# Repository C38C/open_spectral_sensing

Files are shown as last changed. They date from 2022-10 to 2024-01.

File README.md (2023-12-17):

# Open Spectral Sensing

## Table of Contents
1. [About the Project](#about-the-project)
1. [Overview](#overview)
1. [Getting Started](#getting-started)
1. [Capturing Data](#capturing-data)
1. [Build Guide](#build-guide)
1. [Calibration](#calibration)
1. [Troubleshooting](#troubleshooting)
1. [Credits](#credits)

<h2 id="about-the-project">About the Project</h2>
Visible light is made up of several individual wavelengths, each with their own power level. By measuring the power distribution of light throughout the spectrum, we can begin to identify light and quantify its qualities. A spectral sensor measures the power levels at each wavelength. This data can be used for various use-cases such as in colour calibration, agriculture, health, and more. 

<h2 id="overview">Overview</h2>
The sensor is programmed using Arduino (C++) and communicates via a Python program. The sensor consists of off-the-shelf components from SparkFun, and a spectral sensor from nanoLambda - producing an easy-to-assemble spectral sensing device. The goal of this project is to create an open-source and affordable spectral sensing device in order to make light research more accessible.

<h2 id="getting-started">Getting Started</h2>

For wiring, and assembly instructions, see the [Build Guide](#build-guide).

<h3>Installation</h3>

- You must first install the firmware onto the device using provided [compiled binaries](https://github.com/C38C/open_spectral_sensing/releases) by following the instructions below:
    
    - Connect the sensor to a computer via USB
    - With the sensor powered on, double tap the RESET button on the side. (If the sensor is enclosed in the case, you can use an M2 allen-key through the provided hole on the side of the case). This will bring up the "NRF52BOOT" sensor folder.
    - Drag and drop the compiled binary (.uf2) file into this new folder. The sensor will automatically disconnect and update the firmware.
    - Disconnect and reconnect the sensor.

- To connect to the sensor using ```dock.py```, first install matplotlib and pySerial.
```
$ pip install matplotlib
$ pip install pyserial
```

- (Optional) To build your own firmware using the provided source, you must install Arduino IDE and the following libraries:

    - Install Arduino IDE: https://www.arduino.cc/en/software
    - NSP32-Library: https://github.com/arsalan1322/NSP32-Library
    - Installing the Arduino Core for nRF52 Boards: https://learn.sparkfun.com/tutorials/nrf52840-development-with-arduino-and-circuitpython
    - Time library: https://github.com/PaulStoffregen/Time

<h3>Usage</h3>

Once you have assembled the sensor, and flashed the firmware, and installed the required Python packages, you can connect to it using the ```dock.py``` program.
```
$ python dock.py
```
The program will begin looking for a connected spectral sensor, connect to it, then display the menu below. From this menu, you can see the sensor name, sensor port, the current status of the sensor, as well as the current recording interval in ms. You can also start a manual recording, or change other sensor settings. 

```
Refreshed.
---
Selected device: NSP_A on port: COM20.
Currently PAUSED. Recording interval is set to 60000
---
[1] START_RECORDING
[2] MANUAL_CAPTURE
[3] EXPORT_ALL (0 entries)
[4] ERASE_STORAGE
[5] SET_COLLECTION_INTERVAL
[6] SET_DEVICE_NAME
[7] SET_CALIBRATION_FACTOR
[8] RESET_DEVICE
[9] DISCONNECT
[10] CONFIGURE_NSP
[11] REFRESH
Choose a command by entering the number in front
>
```
From here, you can enter ```10``` to enter ```CONFIGURE_NSP``` which will guide you through setting up the sensor for quickly capturing data. 

Alternatively, you can set the recording interval by entering ```5```, then start the recording by entering ```1```. Then, you can disconnect the device by entering ```9```. This step does not set the device name, and uses default capture settings.

At this point, you can disconnect the USB cable if the device is already connected to the battery. The device will continue to collect data according to the interval you set. 

<i>Note that if the device powers off somehow due to a disconnected battery or lack of charge, it will stop recording until started again through</i> ```dock.py```.

<h4>Reading Data </h4>

Enter ```3``` to export all data stored on the device onto the connected computer. Look for a "data" folder in the same directory as ```dock.py```. 

For large files that contain over 500 data points, it is recommended to read data directly off the microSD by ejecting it from the sensor. The microSD can be accessed by removing the cap only.

<h4>Data Structure</h4>

Data is stored on the sensor in a CSV format. There are 146 columns. Columns 1 - 11 hold information about the spectral measurement, and columns 12 - 146 hold the spectral power distribution at 5 nm intervals from 340 nm to 1010 nm. Each row is a unique captured data point.

| Column # | Column title | Example data | Range    | Description                                                                                                       |
|----------|--------------|--------------|----------|-------------------------------------------------------------------------------------------------------------------|
| 1        | DATE         | 05/10/2022   | -        | The date on which this data point was captured. |
| 2        | TIME         | 12:30:37     | -        | The time on which this data point was captured. |
| 3        | MANUAL       | 1            | 0 or 1   | Was this data point captured manually? 1 if yes, 0 if no. |
| 4        | INT_TIME     | 448          | 1 - 1000 | The integration time used for this data point. Exposure time (ms) = (896*[IntegrationTime] + 160) / 500 |
| 5        | FRAME_AVG    | 3            | 1 - 10   | How many frames where averaged for this data point. |
| 6        | AE           | 1            | 0 or 1   | Was auto-exposure enabled? 1 fi yes, 0 if no. |
| 7        | QUALITY      | 0            | -1 to 1   | Indicates whether data point was captured under poor lighting conditions. -1 means too dark, 0 is normal, 1 is too bright. Data points that are not 0 should be discarded. |
| 8        | X            | 38.61        | -        | CIE1931 X value. |
| 9       | Y            | 37.52        | -        | CIE1931 Y value. |
| 10       | Z            | 21.73        | -        | CIE1931 Z value. |
| 11 - 145       | 340 - 1010            |  -       | -        | spectral power in W/m<sup>2</sup>. |

<h4>Charging</h4>

The device will automatically turn off when the battery voltage is too low. Simply plug the sensor into a computer via USB to begin charging. See [LEDs](#leds) for charging indicator.

<h4 id="leds">LEDs</h4>

The sensor has three on-board LEDs: red, blue, and orange. The red LED is always on when the sensor is powered on. The orange LED is only on when the battery is charging, off when charge complete or battery is not connected. 

The blue LED behaviour can be classified using the following list:

- Solid on when sensor has not been setup and it is not recording.
- On for a brief moment while sensor is collecting data, off otherwise.
- Flashes to indicate a problem. See [Troubleshooting](#troubleshooting).

<h2 id="capturing-data">Capturing Data</h2>

There are two ways to capture data using the sensor.

<h3>Automatic and Manual Capture</h3>

<h4>Automatic</h4>

Automatic capture is when you plug in the device, and start recording via the ```START_RECORDING``` menu option in ```dock.py```. The recording interval must be set. Recording will last until stopped via the dock program, or if power is lost.

<h4>Manual Capture</h4>

With the device plugged in and connected to the dock program, you can initiate a data point capture by selecting ```[2] MANUAL_CAPTURE```. A recording interval does not need to be set for this mode. The device will capture one measurement and save it to device memory.

With this feature, you can also preview a graph of the data point once captured. 

<h3>Reading Data</h3>

Data is stored in a CSV file on the microSD card. Data can be read directly from the microSD card, or through the ```EXPORT_ALL``` option via the dock program.

<h2 id="build-guide">Build Guide</h2>

<h3>Parts List</h3>

Electronics

1. [nanoLambda NSP32m W1](https://nanolambda.myshopify.com/products/nsp32m_w1_temp)
2. [SparkFun Pro nRF52840 Mini](https://www.sparkfun.com/products/15025)
3. [SparkFun microSD Transflash Breakout](https://www.sparkfun.com/products/544)
4. 2GB+ microSD card
5. [800mAh Li-Po battery with 2mm JST connector](https://www.solarbotics.com/product/17804)
6. [30 AWG Silicone Wire](https://www.amazon.ca/gp/product/B01M70EDCW/ref=ppx_yo_dt_b_asin_title_o04_s00?ie=UTF8&psc=1)

Hardware (optional)

6. [3D printed case ]() (Found in ```3D Models\Case```)
7. [2x] M2 bolts and [2x] nuts (for cap)
8. [4x] 4x1.7mm cylindrical magnets

<h3 id="wiring-diagram">Wiring Diagram</h3>

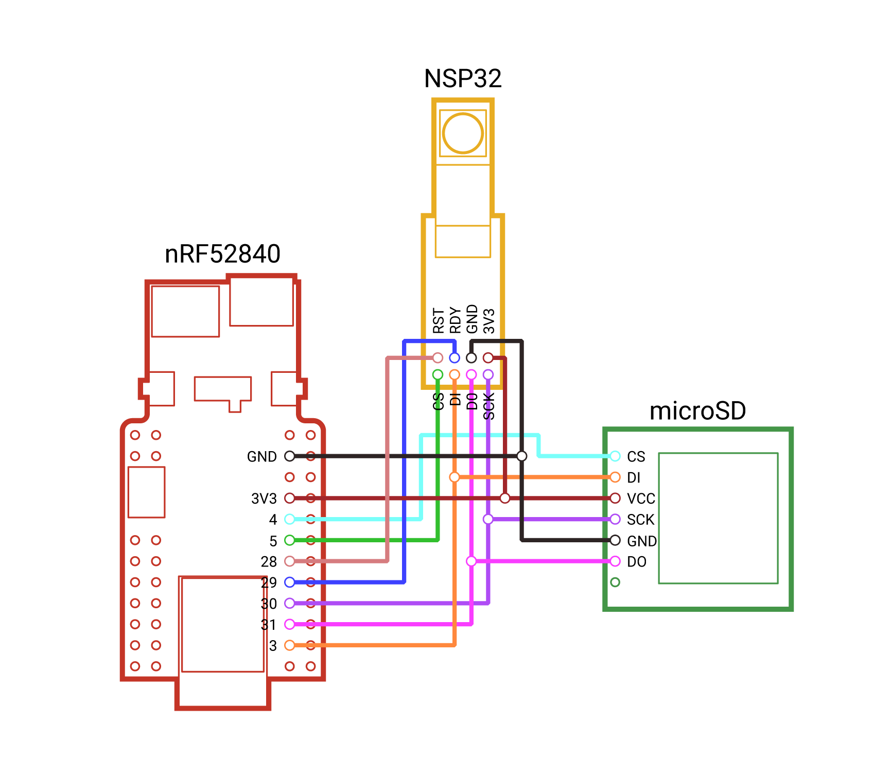
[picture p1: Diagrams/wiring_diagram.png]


<h3 id="layout">Layout</h3>

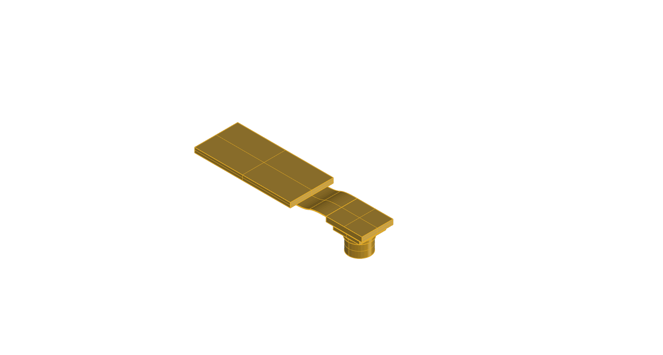
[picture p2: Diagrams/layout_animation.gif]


<h3>Soldering</h3>

To allow for a small device footprint, flexible 30 AWG silicone wire is used. Approximately 60 cm of wire is used for the configuration outlined in [Layout](#layout)

Soldering happens from both the top and bottom of the nRF52840. "Helping hands" are highly recommended, as well as a fine-tip soldering iron.

Use the following table to help cut, match, and solder wires:

| Wire  # | Length for SD (mm) | Length for NSP (mm) | Pin on nRF52840 | Pin on microSD card reader | Pin on nanoLambda NSP32m |
|---------|--------------------|---------------------|-----------------|----------------------------|--------------------------|
| 1       | 20                 | 55                  | GND             | GND                        | GND                      |
| 2       | 25                 | 50                  | 3V3             | VCC                        | 3V3                      |
| 3       | 20                 | -                   | 4               | CS                         | -                        |
| 4       | -                  | 45                  | 5               | -                          | CS                       |
| 5       | -                  | 45                  | 28              | -                          | RST                      |
| 6       | -                  | 40                  | 29              | -                          | RDY                      |
| 7       | 40                 | 45                  | 30              | SCK                        | SCK                      |
| 8       | 50                 | 35                  | 31              | DO/MISO                    | DO/MISO                  |
| 9       | 40                 | 45                  | 3               | DI/MOSI                    | DI/MOSI                  |

Wires for the microSD card reader are soldered from the bottom, wires for the NSP32m are soldered from the top.
Two wires connect to single common pins on the nRF52840 for GND, 3V3, SCK, DO, and DI.

<h3>3D Printing</h3>

The case consists of three separate parts that come together to enclose the sensor. They are located in the ```3D Models\Case``` directory.

<h4>Material</h4>
PETG (recommended), PLA, ABS, etc. Recommended material is PETG due to its flexibility. PLA and ABS can be used, but repeated strain may cause parts to snap.

<h4>Layer height</h4>
0.12 mm or finer.

<h4>Supports</h4>
Yes, as shown in orange.

<h4>Part orientation</h4>

**If using FDM printer, the part orientation is important for maximum strength.**

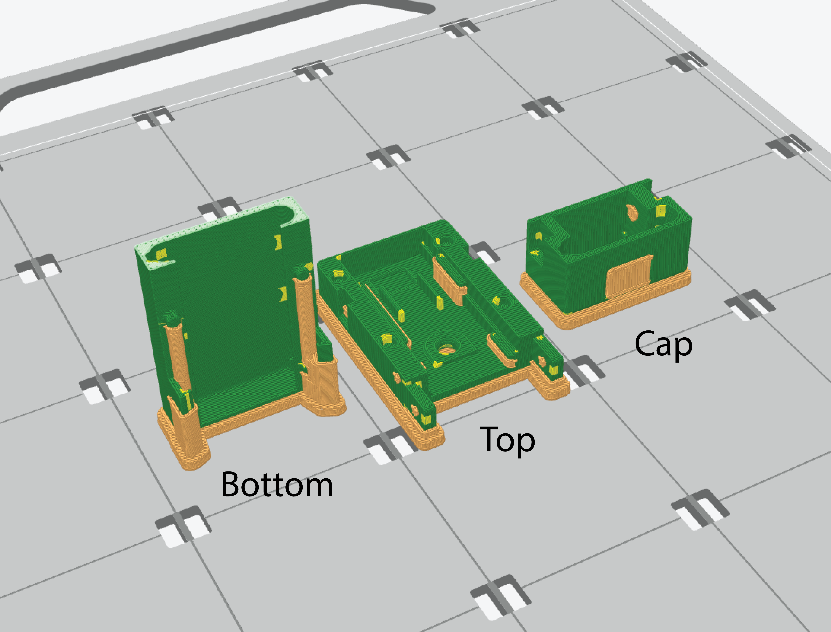
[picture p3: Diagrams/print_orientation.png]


<h3>Assembly</h3>

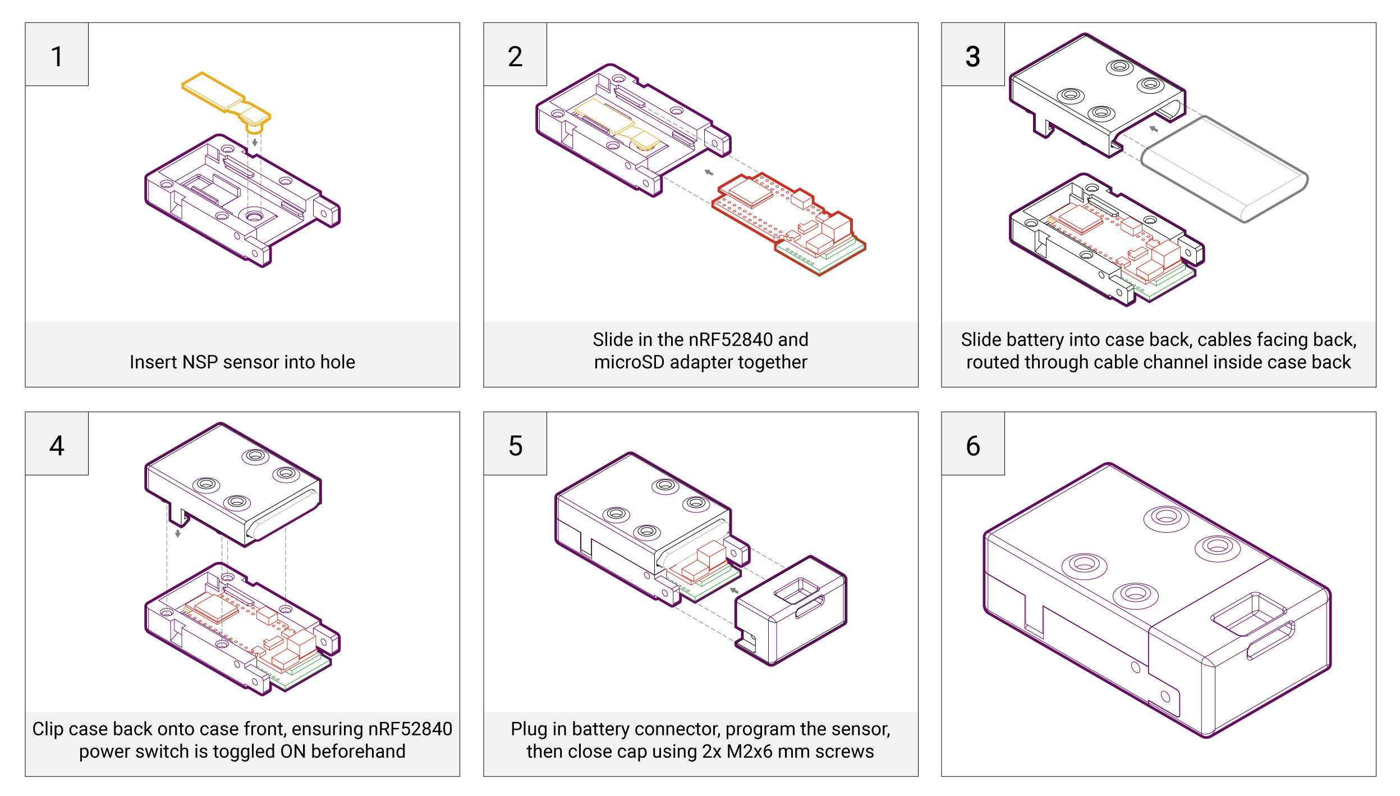
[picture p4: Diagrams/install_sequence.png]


&nbsp;

1. Insert the NSP32m sensor through the hole in the ```top``` part of the case
2. Slide in the nRF52840 while gently pushing down the NSP32m, ensuring the microSD reader slides in to its slot when the nRF52840 is half-way inserted.
3. Slide the battery into the ```bottom``` part of the case as shown. The cable will come around to the front through the channel on the side.
4. Snap together both the ```bottom``` and ```top``` parts of the case, making sure the silicone wires are out of the way.
5. Fit two M2 hex bolts into the ```cap```. They are compression fit.
6. **Before installing the ```cap```, make sure to program the sensor, as the USB port is inaccessible with the ```cap``` on.**
6. *Once the sensor has been programmed*, slide the ```cap``` onto the case, lining up the forks on the sides.
7. Screw in two M2x8mm bolts through the forks. 
8. (optional) Insert lanyard loop.

*The sensor is not waterproof, please keep it dry.*

<h2 id="calibration">Calibration</h2>

If you are using a non power-calibrated (NPC) sensor from nanoLambda, you must calibrate it against another calibrated sensor and update the calibration factor within your NPC sensor. Use the ```SET_CALIBRATION_FACTOR``` option inside the dock program.

<h2 id="troubleshooting">Troubleshooting</h2>

<h3>Blue LED flashes once: Problem with SD card.</h3>

1. Check if SD card is inserted
2. Plug in SD card to computer and delete all files stored on it

<h3>Blue LED flashes twice: Problem with internal memory</h3>

1. Connect the sensor to ```dock.py```
2. Select ```RESET_DEVICE``` by entering ```4```

<h2 id="resources">Resources</h2>
<ul>
<li>Microsoft UF2: <a href="https://github.com/microsoft/uf2">https://github.com/microsoft/uf2</a></li>
</ul>

<h2 id="credits">Credits</h2>

- J. Alstan Jakubiec
Assistant Professor, Daniels Faculty of Architecture + School of the Environment
alstan.jakubiec@daniels.utoronto.ca
- Sadi Wali
Research Assistant, B.A.Arch
- Arsalan Khan
B.A.Sc. Physics and Computer Science Student

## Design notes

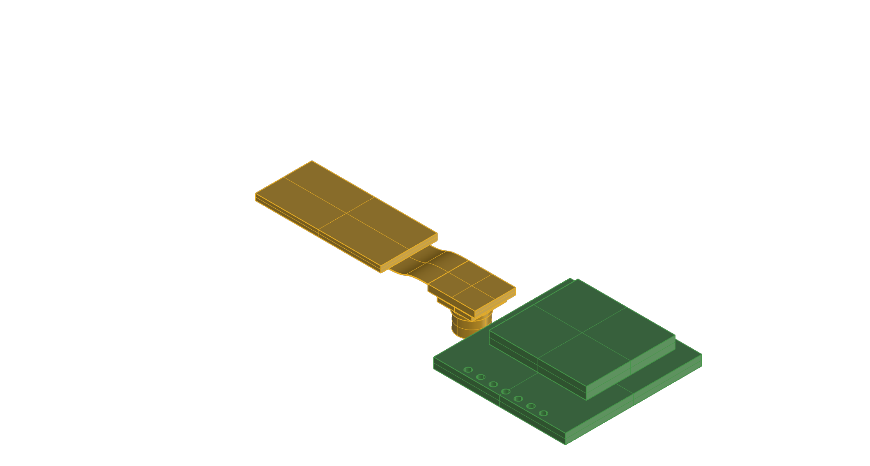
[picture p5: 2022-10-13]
Diagrams/layout_2.png

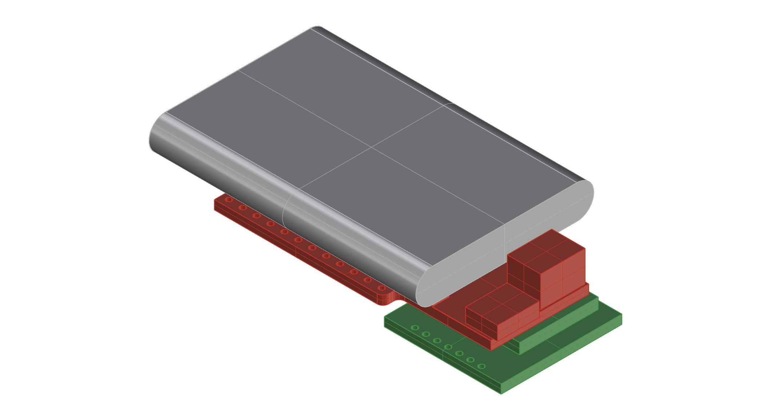
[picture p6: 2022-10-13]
Diagrams/layout_4.png

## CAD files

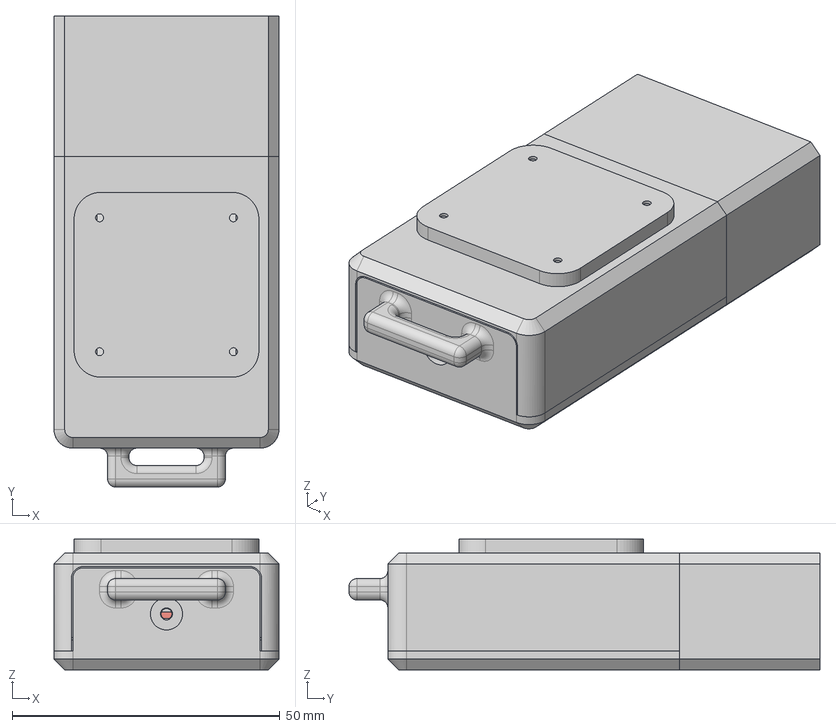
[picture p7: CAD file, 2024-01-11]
3D Models/Case V2/OOSI_CASE_V2.step
42.0 x 87.9 x 24.4 mm
Battery
SD
NL
nrf52
CASE_A
CASE_B
backplate
cover
SD_CARD_PROTECTOR

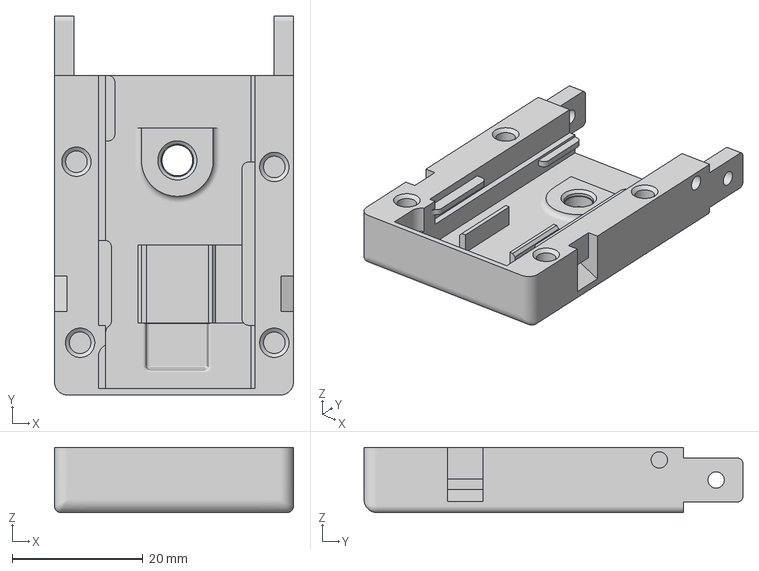
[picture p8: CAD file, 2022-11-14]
3D Models/Case/case_front.3mf
36.6 x 58.0 x 10.0 mm

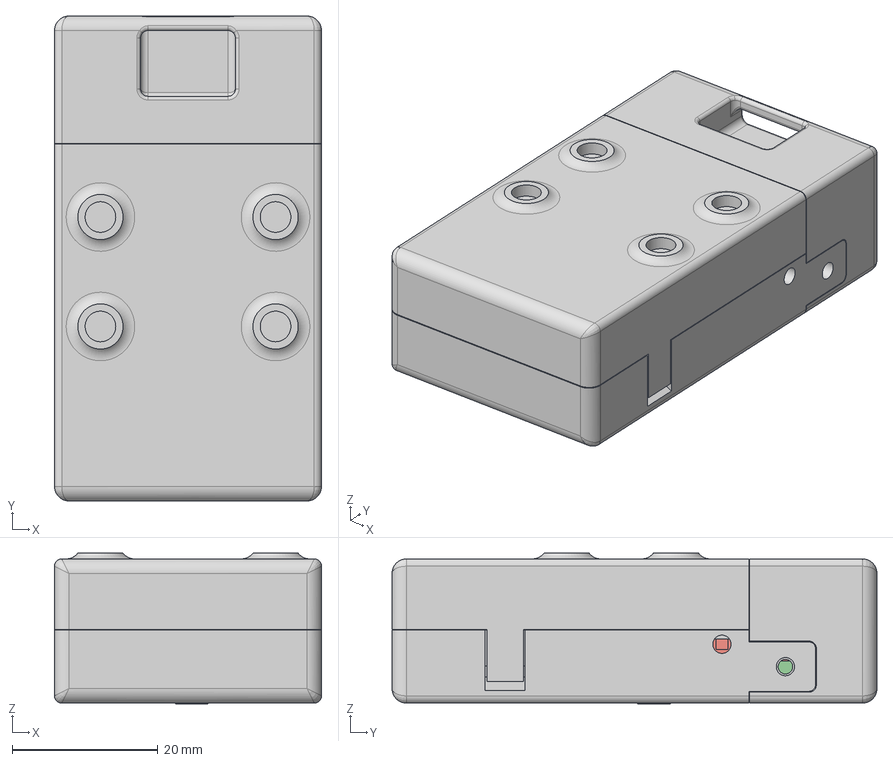
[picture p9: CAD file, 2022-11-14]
3D Models/Case/open_spectral_sensor_case_v1.step
36.6 x 66.5 x 20.7 mm
Battery
SD
NL_1
nrf52
Case Back
Case Cap
Case Front

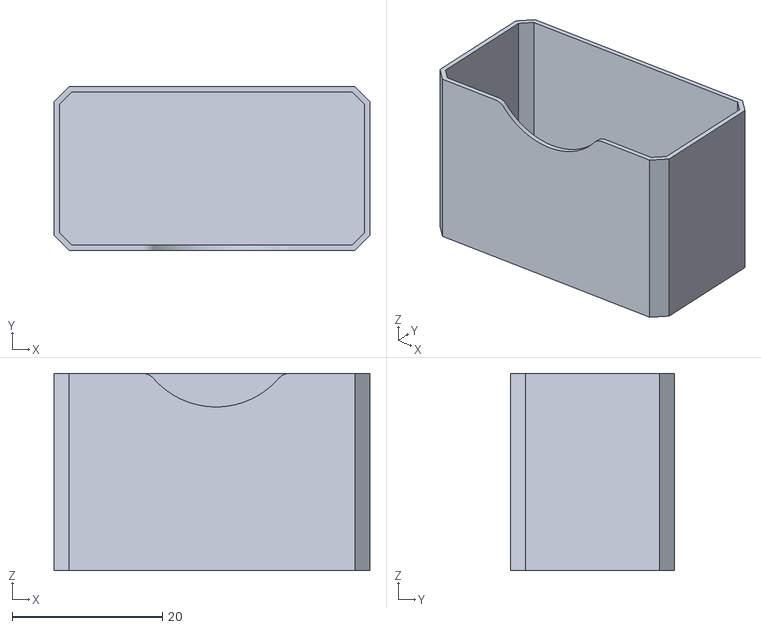
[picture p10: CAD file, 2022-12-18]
3D Models/Case V2/CASE_CAP.stl
42.0 x 21.8 x 26.2

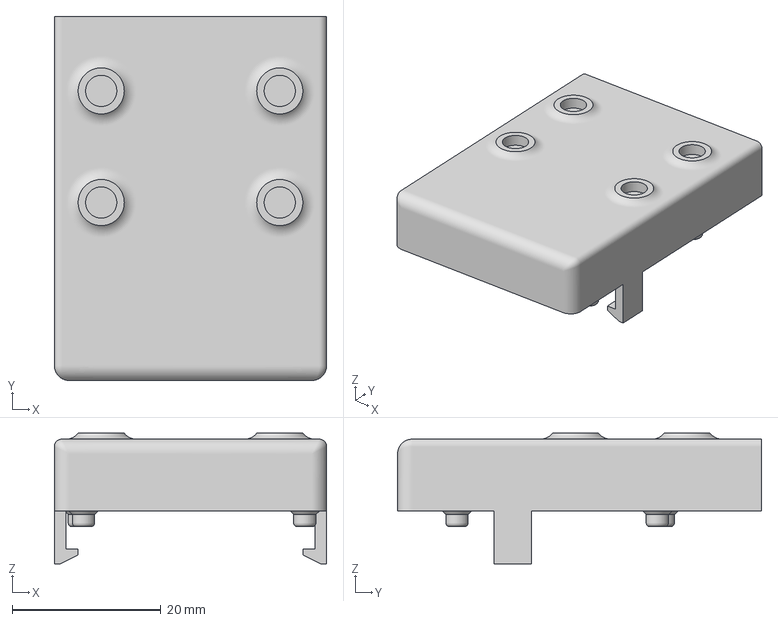
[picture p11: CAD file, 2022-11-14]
3D Models/Case/case_back.3mf
36.6 x 48.9 x 17.6 mm

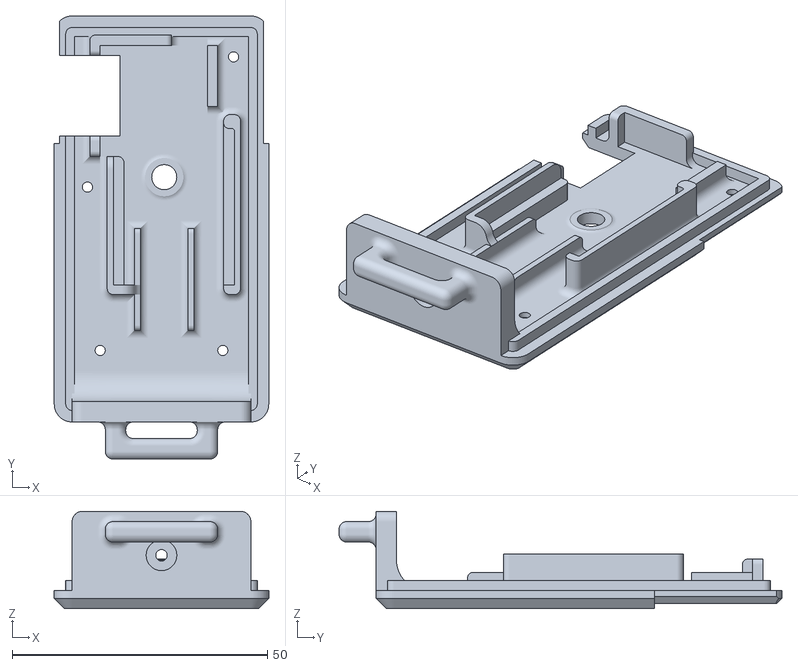
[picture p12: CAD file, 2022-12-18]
3D Models/Case V2/CASE_FRONT.stl
42.0 x 86.7 x 19.0

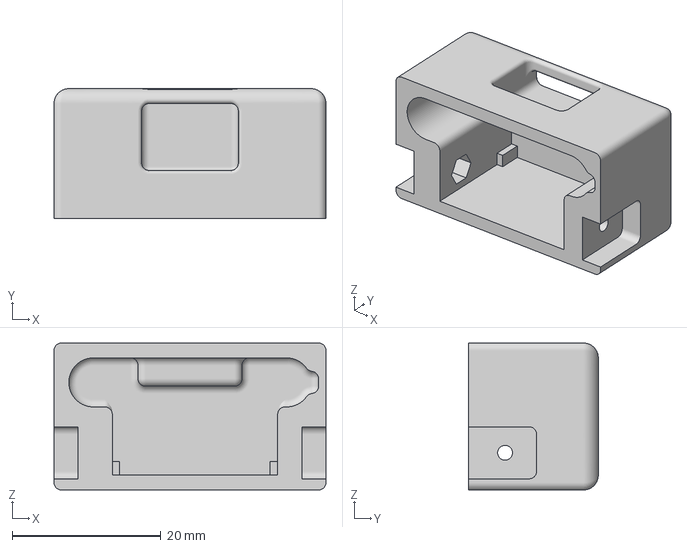
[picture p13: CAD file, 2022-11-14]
3D Models/Case/case_cap.3mf
36.6 x 17.4 x 19.8 mm

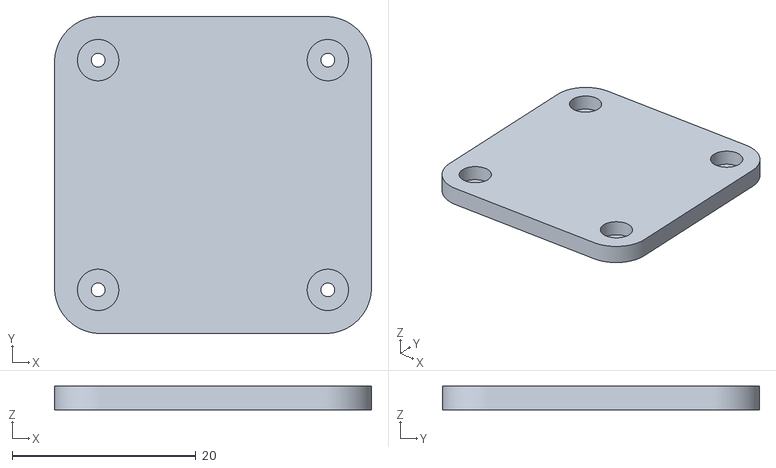
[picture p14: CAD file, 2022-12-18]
3D Models/Case V2/CASE_MAGNETIC_BACKPLATE.stl
34.5 x 34.5 x 2.60

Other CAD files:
3D Models/Case V2/CASE_SDCARD_HOLDER.stl
3D Models/Case V2/OOSI_CASE_V2.f3d
3D Models/Case/open_spectral_sensor_case_v1.f3d

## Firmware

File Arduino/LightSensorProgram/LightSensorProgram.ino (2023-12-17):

/**
 * Sadi Wali August 2022
 * Last modified: December 16 2023
 * 
 * This open-source program is written for the Nordic nRF52840, and the NanoLambda NSP32m W1
 * to create a lightweight wearable spectral sensor that record data at a set interval on battery.
 * 
 * Pin layout used:
 * ------------------------------------
 *               NSP32      Sparkfun       
 * SPI                      nRF52840     
 * Signal        Pin          Pin        
 * ------------------------------------
 * Wakeup/Reset  RST          28    
 * SPI SSEL      SS           5    
 * SPI MOSI      MOSI         3    
 * SPI MISO      MISO         31  
 * SPI SCK       SCK          30   
 * Ready         Ready        29
 * ------------------------------------
 *               SD Card
 *               Pin
 * ------------------------------------
 * SPI SSEL      CS           4
 * SPI MOSI      DI           3
 * SPI MISO      DO           31
 * SPI SCK       SCK          30
 * 
 * 
 * 
 * Error codes:
 * ------------------------------------
 * 
 * Error         Number of
 *               flashes
 * ------------------------------------
 * SD card       1
 * Internal FS   2
 * 
 * 
 **/

#include "Adafruit_TinyUSB.h"                       // for serial communication on nrf52840

#include <SPI.h>                                    // Arduino SPI

#include <TimeLib.h>                                // Date and time

#include <ArduinoAdaptor.h>                         // for low-level interfacing with the NSP via Arduino

#include <NSP32.h>                                  // for high-level interfacing with the NSP module

#include "DataStorage.h"                            // SD Data storage module

#include "Constants.h"                              // constants

#include <Adafruit_LittleFS.h>                      // persistent data storage

#include <InternalFileSystem.h>                     // persistent data storage

using namespace NanoLambdaNSP32;
using namespace Adafruit_LittleFS_Namespace;

const unsigned int PinRst = NSP_RESET;              // pin Reset
const unsigned int PinSS = NSP_CS_PIN;              // NSP chip select pin
const unsigned int PinReady = NSP_READY;            // pin Ready

// VARIABLES
int logging_interval = DEF_CAPTURE_INTERVAL;        // the data logging interval
unsigned long last_collection_time = 0;             // remember the last collection interval
unsigned long time_offset = 0;                      // how much time to offset by if device hung for long operations
bool recording = false;                             // is data capture recording?
String device_name = DEV_NAME_PREFIX;               // the device name for easier identification
double calibration_factor = DEF_CALIBRATION_FACTOR; // the calibration factor
int int_time = 500;                                 // default integration time for sensor           
int frame_avg = DEF_FRAME_AVG;                      // how many frames to average
bool ae = true;                                     // use autoexposure?
unsigned int data_counter = 0;                      // how many data points collected and stored
int s_dark_readings = 0;                            // how many sequential dark readings?
unsigned long paused_time = 0;                      // when was the sensor paused
unsigned long pause_duration = 0;                   // how long was the sensor paused for?

char ser_buffer[32];                                // the serial buffer
int read_index = 0;                                 // the serial buffer read index

// OBJECTS
ArduinoAdaptor adaptor(PinRst, PinSS);              // master MCU adaptor
NSP32 nsp32( & adaptor, NSP32::ChannelSpi);         // NSP32 (using SPI channel)
Storage st(SD_CS_PIN, LOG_FILENAME);                // the data storage object
Adafruit_LittleFS_Namespace::File file(InternalFS); // the metadata file stored in persistent flash


/* Arduino setup function. */
void setup() {
  pinMode(PinReady, INPUT_PULLUP); // use pull-up for ready pin
  pinMode(7, OUTPUT); // onboard LED output
  digitalWrite(7, HIGH); // turn LED ON
  attachInterrupt(digitalPinToInterrupt(PinReady),
    PinReadyTriggerISR, FALLING); // enable interrupt for NSP READY
  // initialize serial port
  Serial.begin(BAUDRATE);

  // initialize the persistent storage
  InternalFS.begin();

  // read persistent flash storage into memory
  read_memory();

  // if the SD storage object is errored, go into error state
  if (!st.init()) error_state(1);

  // initialize NSP32
  nsp32.Init();
  nsp32.Standby(0);

  // if device is already recording on startup, that means power was lost
  if (recording) {
    String error_line = "POWER LOSS DETECTED";
    st.write_line(& error_line);
  }
  
}

/* Get a reading from the NSP32 sensor */
void read_sensor(SpectrumInfo * info, int use_int_time = 0, int use_frame_avg = 3, bool use_ae = true) {
  // wakeup the sensor if sleeping
  nsp32.Wakeup();
  // get the spectrum data. Note that if ae is true, int_time is ignored
  nsp32.AcqSpectrum(0, use_int_time, use_frame_avg, use_ae);
  // wait until spectrum data completely collected
  while (nsp32.GetReturnPacketSize() <= 0) nsp32.UpdateStatus();
  // data has been collected, extract into info
  nsp32.ExtractSpectrumInfo(info);
}

/* Check if datapoint is too dark, okay, or too bright indicated by -1, 0, 1 respectively */
int validate_reading(SpectrumInfo infoS) {

  // count the number of dips to zero. A dark reading will have multiple dips
  int dip_count = 0;
  bool is_zero = false;
  
  // go through 400 - 700 nm, and count how many times the graph dips to 0
  for (int i = (400 - MIN_WAVELENGTH) / 5; i < (700 - MIN_WAVELENGTH) / 5; i++) {
     if (infoS.Spectrum[i] == 0) {
      if (!is_zero) {
        dip_count++;
        is_zero = true;
      }
     } else {
      is_zero = false;
     }
  }

  // combine the dip count with autoexposure malfunction with low CIE1931 Y value 
  if (infoS.IntegrationTime == 1 || infoS.Y <= MIN_ACCEPTABLE_Y || dip_count >= 2) {
    // too dark
    return -1;
  } else if (infoS.IsSaturated == 1) {
    // too bright
    return 1;
  } else {
    // just right
    return 0;
  }
}

/* Take a manual or automatic measurement, and return the formatted datapoint line */
String take_measurement(bool manual_measurement = false) {
  SpectrumInfo infoS; // variable for storing the spectrum data

  bool dark_flag = true;
  bool too_dark = false;
  bool second_attempt = false;

  // modified settings to use in this session
  int mod_int_time = int_time;
  int mod_frame_avg = frame_avg;
  bool mod_ae = ae;

  while (true) {

    read_sensor( & infoS, mod_int_time, mod_frame_avg, mod_ae);
    
    // validate the datapoint
    int validation_res = validate_reading(infoS);

    if (validation_res == 1) {
      // too bright, nothing to do
      s_dark_readings = 0;
      break;

    } else if (validation_res == -1) {
      // too dark
      
      if (ENABLE_NIGHTMODE && s_dark_readings >= MAX_DARK_READINGS) {
        // too many dark readings in a series
        
        if (!second_attempt) {
          // this was the first attempt, set int_time to 500, and try again
          mod_ae = false;
          second_attempt = true;
          mod_int_time = STARTING_DARK_INT_TIME;
          continue;
          
        } else {
          // this was the second attempt, environment still too dark so don't continue
          too_dark = true;
          break;
          
        }
      }

      // too dark even with int_time maxed
      if (mod_int_time >= MAX_INT_TIME) {
        too_dark = true;
        s_dark_readings++;
        break;
      }

      // find the correct exposure time, use half the frames to save time and power
      mod_ae = false;
      mod_frame_avg = frame_avg / 2;

      if (mod_frame_avg < 1) mod_frame_avg = 1;

      if (dark_flag) {
        // this flag is used to set integration time to 500 only once
        dark_flag = false;
        mod_int_time = STARTING_DARK_INT_TIME;
        continue;
      }

      mod_int_time += 100;

    } else {
      // no issues, break out of loop 
      s_dark_readings = 0;
      break;
    }
  }

  // format each line of CSV file into this line
  String line = format_line(infoS, manual_measurement, too_dark, mod_frame_avg, mod_ae);

  // Standby seems to clear SpectrumInfo, therefore call it after processing the data
  nsp32.Standby(0);

  // write the data to the SD card, if there is an error, try to restart SD
  while (!st.write_line( & line)) {
    digitalWrite(7, HIGH);
    // wait 1 second, and try initialize SD again
    delay(1000);

    if (st.init()) {
      // write the line
      st.write_line(& line);
      // write that there was an error
      String error_line = "DATA LOGGING ERROR";
      st.write_line(& error_line);
      digitalWrite(7, LOW);
      // break out of the loop
      break;
    }
  }

  data_counter++;
  update_memory();

  return line;
}

String format_line(SpectrumInfo infoS, bool manual_measurement, bool too_dark, int mod_frame_avg, int mod_ae) {
  String line = "";

  // 1. Which date was this data point collected on?
  if (day() < 10) line += "0";
  line += String(day());
  line += "/";
  if (month() < 10) line += "0";
  line += String(month());
  line += "/";
  line += String(year());
  line += ",";

  // 2. When was this data point collected?  
  if (hour() < 10) line += "0";
  line += String(hour());
  line += ":";
  if (minute() < 10) line += "0";
  line += String(minute());
  line += ":";
  if (second() < 10) line += "0";
  line += String(second());
  line += ",";

  // 3. Was this recording triggered manually?
  line += String(manual_measurement);
  line += ",";

  // 4. What integration time was used?
  line += String(infoS.IntegrationTime);
  line += ",";

  // 5. What frame average number was used?
  line += String(mod_frame_avg);
  line += ",";

  // 6. Was auto-exposure used?
  line += String(mod_ae);
  line += ",";

  // 7. What was the light quality? A dark reading will be -1, a good reading is 0, and a saturated reading is 1'
  if (infoS.IsSaturated) {
    line += "1";
  } else if (!infoS.IsSaturated && too_dark) {
    line += "-1";
  } else if (!infoS.IsSaturated && !too_dark) {
    line += "0";
  } else {
    line += "-2";
  }
  line += ",";

  // 8. Then put in the CIE1931 values
  line += String(infoS.X, CIE_PRECISION);
  line += ",";
  line += String(infoS.Y, CIE_PRECISION);
  line += ",";
  line += String(infoS.Z, CIE_PRECISION);
  line += ",";

  // 9. Then put in the spectrum data. Sensor reads 340-1010 nm (inclusive) in 5 nm increments
  for (int i = ((MIN_WAVELENGTH - SENSOR_MIN_WAVELENGTH) / WAVELENGTH_STEPSIZE); i <= ((MAX_WAVELENGTH - SENSOR_MIN_WAVELENGTH) / WAVELENGTH_STEPSIZE); i++) {
    line += String(infoS.Spectrum[i] * calibration_factor, CAPTURE_PRECISION);
    line += ",";
  }

  return line;
}

/* Update the persistent storage */
void update_memory() {
  // overwrite the file
  String filename = "/" + String(METADATA_FILENAME) + String(FILE_EXT);
  InternalFS.remove(filename.c_str());
  if (file.open(filename.c_str(), FILE_O_WRITE)) {
    String writeline = device_name + "," + String(logging_interval) + "," + String(data_counter) + "," + String(calibration_factor) + "," + String(recording);
    file.write(writeline.c_str(), strlen(writeline.c_str()));
    file.close();

  } else {
    // could not create file
    error_state(2);
  }
}
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

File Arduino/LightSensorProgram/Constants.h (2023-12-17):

#ifndef CONSTANTS_H
#define CONSTANTS_H

// STORAGE
#define LOG_FILENAME "LOG2"             // the log filename to write to
#define METADATA_FILENAME "METADATA"    // the metadata file name
#define FILE_EXT ".CSV"                 // the log file extension
#define MAX_LINE_LENGTH 3000            // the maximum line length in file

// SERIAL COMMUNICATIONS
#define DEV_NAME_PREFIX "NSP"           // the device name prefix
#define BAUDRATE 921600                 // the device baudrate for serial communication

// DEVICE SETTINGS
#define DEF_CAPTURE_INTERVAL 60000      // how frequently to capture data in ms
#define SLEEP_DURATION 5000             // how many ms to go into deep sleep for in between wake checks
#define MIN_WAVELENGTH 340              // the minimum wavelength we are interested in
#define MAX_WAVELENGTH 1010             // the maximum wavelength we are interested in
#define DEF_FRAME_AVG 3                 // how many frames to average into single reading
#define CAPTURE_PRECISION 18            // how many digits of precision for SPD values
#define CIE_PRECISION 4                 // how many digits of precision for CIE1931 values
#define DEF_CALIBRATION_FACTOR 1        // the calibration factor for the particular sensor
#define MIN_ACCEPTABLE_Y 5              // the minimum acceptable Y value for reading (CIE1931)
#define STARTING_DARK_INT_TIME 500      // the starting integration time for correcting dark readings
#define MAX_INT_TIME 1200               // the maximm integration time to use
// NIGHT MODE
#define ENABLE_NIGHTMODE true           // night mode attempts to save battery by reducing readings when dark
#define MAX_DARK_READINGS 3             // how many sequential dark readings before nightmode engages?

// NSP SENSOR SETUP
#define SENSOR_MIN_WAVELENGTH 340       // the minimum sensing wavelength (for W1 sensor)
#define SENSOR_MAX_WAVELENGTH 1010      // the maximum sensing wavelength  (for W1 sensor)
#define WAVELENGTH_STEPSIZE 5           // the sensor wavelength resolution (5 nm for W1 sensor)

// PINS
#define SD_CS_PIN 4                     // pin connected to SD CS
#define NSP_CS_PIN 5                    // pin connected to NSP CS
#define NSP_RESET 28                    // NSP reset pin
#define NSP_READY 29                    // NSP ready pin

#endif

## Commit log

2022-09-26 Added 3D models and modified NSP library
    [open_spectral_sensor_case_v1.f3d, open_spectral_sensor_case_v1.step]
2022-09-26 Fixed incorrect variable
    Fixed issue where calibration factor was being set to 0 when set.
2022-09-26 Increased the serial buffer size
    Increased serial buffer size to 32 bytes from 16 bytes in order to allow for the transfer of longer strings of numbers for functions such as updating the calibration factor.
2022-10-05 removed Arduino library
2022-11-01 updated wiring table
2022-11-06 Increased min sleep time to 60s.
    Increased min sleep time to 60s from 1s, which should improve battery life. Due to this change, the sensor will not connect to the dock program without first resetting using the reset button, or by d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
2022-11-14 3D models added
    [case_back.3mf, case_cap.3mf, case_front.3mf, open_spectral_sensor_case_v1.f3d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]
2022-11-14 Set sleep duration to 5s from 1min
    Changing sleep duration did not improve battery life, there is another source of battery drain. Changing it to 5s for improved dock program connection response
2022-12-05 Update Constants.h
    Changed SD file name so there won't be any conflicts caused by new data with 1 fewer column. The sensor will write in a new file.
2022-12-18 new case designs uploaded
    [CASE_CAP.stl, CASE_FRONT.stl, CASE_MAGNETIC_BACKPLATE.stl, OOSI_CASE_V2.f3d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]
2023-01-05 Updated missing body from case step file
    A missing body was hidden during export, this is now included in the step file.
    [OOSI_CASE_V2.step]
2023-12-17 Data recording will not auto pause if SD card ejected
    SD card ejections will be recorded in the CSV file, along with power loss detection. In case of accidental SD card ejection, device will continue capturing data once SD card inserted again. On accide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
2024-01-11 Added SD card holder piece.
    [CASE_SDCARD_HOLDER.stl, OOSI_CASE_V2.f3d, OOSI_CASE_V2.step]
